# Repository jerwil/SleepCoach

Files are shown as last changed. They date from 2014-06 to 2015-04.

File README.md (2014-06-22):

# The Sleep Coach

A small simple device to help users fall asleep. The Sleep Coach was designed to be easy to manufacture, and the design and code are open source (see license at bottom).

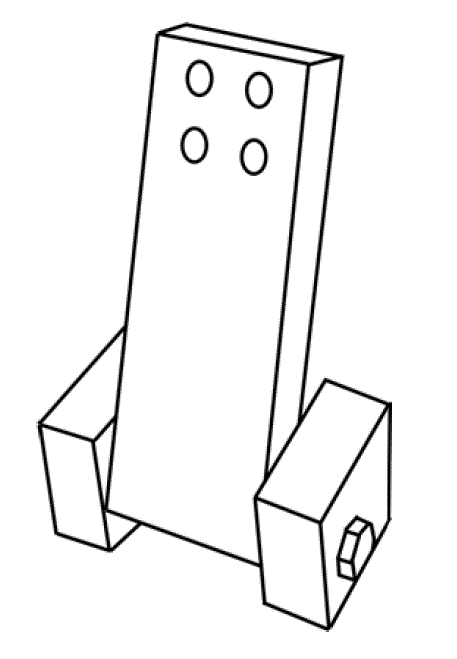
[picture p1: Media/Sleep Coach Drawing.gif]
Sleep Coach Drawing

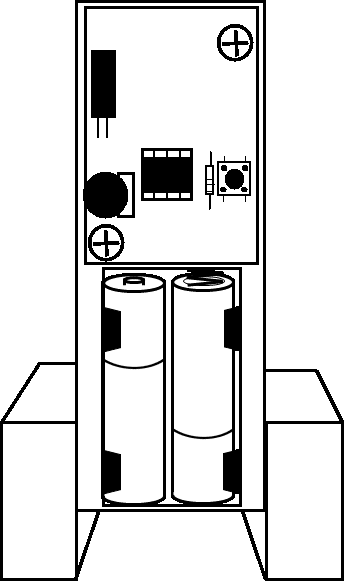
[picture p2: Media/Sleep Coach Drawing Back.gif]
Sleep Coach Back View


## Features

* Creates a pattern of light that you match your breathing to
* Breathing rate is decreased during sleep, so this helps ease you into sleep faster
* The maximum brightness can be adjusted on-the-fly using the wheel potentiometer on the back
* One-button operation

## How to Use

* Set up the sleep coach on a night stand or table next to your bed.
* Turn on the sleep coach and adjust its angle to either shine in your eyes or on a wall or ceiling.
* Begin coaching, and match your breathing to the pattern of light
* Fall asleep faster!

## Demo Video

* [Demo Video](http://youtu.be/cpdKv6ZaVtQ)

## Study

I have been conducting a study to collect data on the Sleep Coach to see if it actually helps users fall asleep.

* [Study Information](http://i.imgur.com/wzw9Kvx.jpg)
* [Study Sign-up link] (http://goo.gl/noJXXP)
* [Study Results So Far] (https://github.com/jerwil/SleepCoach/blob/master/Documentation/Data%20Summary%20-%20Round%202.pdf?raw=true)

So far I have had great success with the sleep coach, but I only have a sample size of 5 users. I'm always looking for more study participants!

## Requirements

### Hardware

* ATtiny85
* 8 pin DIP socket (recommended)
* 1-sided copper board
* 330Ω resistor
* 10 mF capacitor
* 4 red LEDs
* Tact button
* Wheel potentiometer
* Battery holder for 2 AA batteries

For my version of the mechanical design:

* 3.5" 1/4-20 bolt
* 1/4-20 wing nut
* 8 inches of 1.5" x .75" wood

Details on mechanical design to come soon

### Schematics

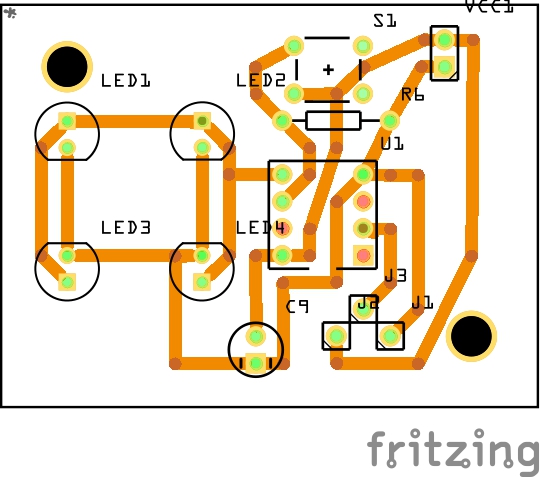
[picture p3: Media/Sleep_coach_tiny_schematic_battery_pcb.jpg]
Sleep Coach schematic


See the included Fritzing diagram (.fzz file) for details.

### License

<br /><span xmlns:dct="http://purl.org/dc/terms/" property="dct:title">MAX7219 Board Schematics</span> by <a xmlns:cc="http://creativecommons.org/ns#" href="www.JeremyAdamWilson.com" property="cc:attributionName" rel="cc:attributionURL">Jeremy Wilson</a> is licensed under a <a rel="license" href="http://creativecommons.org/licenses/by-nc/4.0/">Creative Commons Attribution-NonCommercial 4.0 International License</a>.

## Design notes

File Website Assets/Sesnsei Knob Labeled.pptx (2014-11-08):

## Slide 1

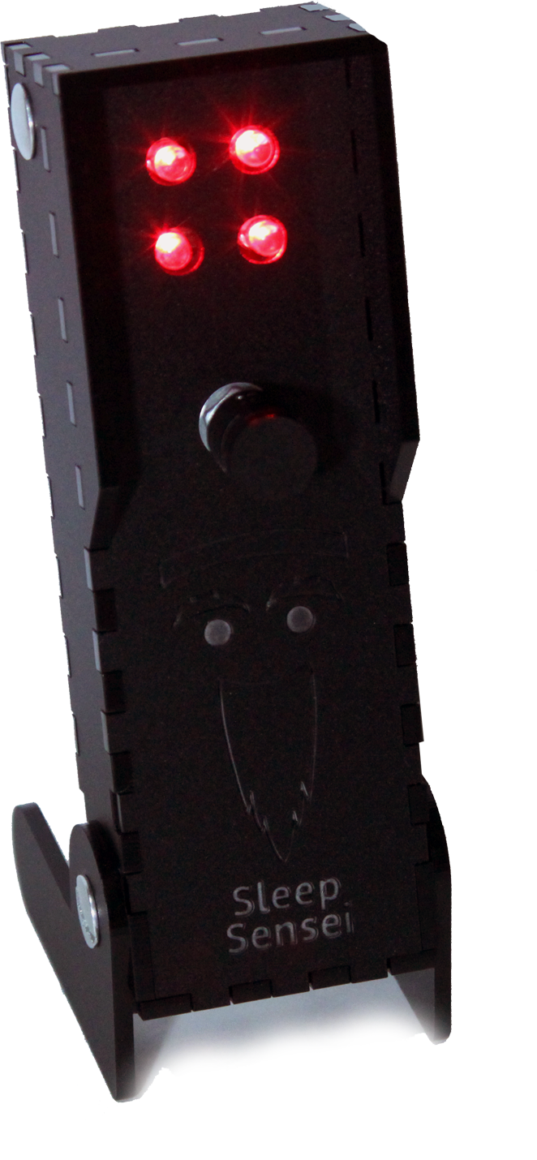
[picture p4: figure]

4 Bright LEDs
So you can be coached with your eyes closed

Side Shields
To cut down stray light

Mode Selection
Choose between profiles

Brightness Adjustment
To account for different tastes

Pivoting Base
Allows you to aim the light where it is needed

NOTE: Functional prototype – not final product

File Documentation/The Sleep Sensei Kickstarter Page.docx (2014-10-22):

# The Sleep Sensei Story

I have trouble falling asleep at night. I used to take over-the-counter remedies, and I've tried prescription stuff, but these either made me feel groggy the next day or had side effects that were not worth the benefits. I then stumbled upon some smartphone apps and devices that use a rising and falling pattern of light to help you get to sleep by training your breathing. I tried these with some success, but I found that they all had one major flaw: they required your eyes to be open. Who in the world tries to fall asleep with their eyes open?!

Using my arduino skills, I set to create a device that will help coach my breathing to ease myself to sleep with my eyes closed. Thus the Sleep Sensei was born, with its pivoting base and 4 ultra-bright red LEDs that can shine through eyelids, it aims to fix the problems of similar apps and devices.

# The Device Design

The Sleep Sensei is designed to shine a pattern of light through your eyelids. This pattern of light is used to coach your breathing pattern, which encourages your breaths to get longer as time progresses. To ensure that enough light is delivered, I put 4 LEDs on the device; however, the maximum brightness is adjustable to account for different tastes. In order to account for different heights of nightstands, I made the device able to pivot to encompass a wide range of scenarios. For those that sleep with a partner, I added side-shields to better concentrate the light to reduce any stray light that may annoy others.

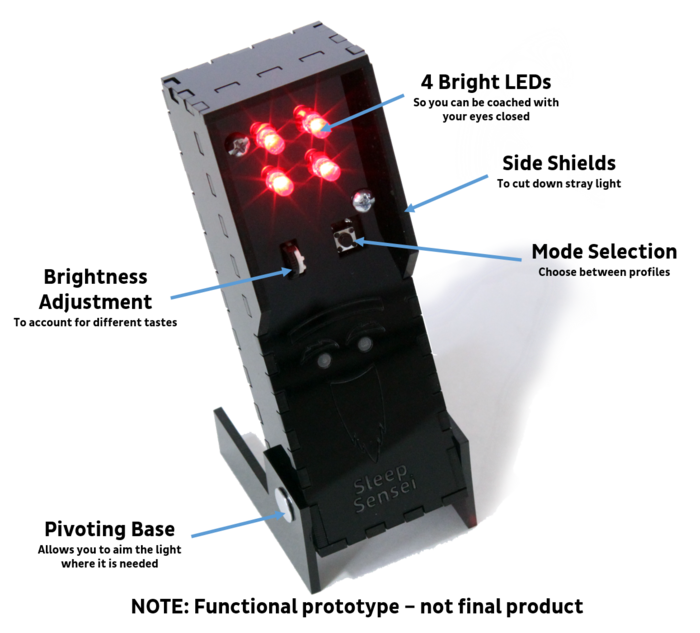
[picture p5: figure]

I chose laser cutting to make the kit easy to ship and mass produce. With the goal order volume (around 1000 units), laser cutting proved to be an affordable way to make a custom design.

The circuit board was designed with fritzing, and the logic and programming were done with arduino, which are both open source tools.

All aspects of the design (arduino code, circuit board designs, mechanical design files, website assets, photos, and documentation) are open source and are available on my github page (https://github.com/jerwil/SleepCoach). I will continue to refine the design and produce more prototypes using the Kickstarter funding, and during the development time, I encourage advanced users to fork the repository and provide me with suggestions and ideas to include in the final product!

# How it Works

The Sleep Sensei works by reducing your breathing rate, causing increased relaxation and bringing your breathing pattern closer to the reduced breathing pace that comes with sleep. It also has the benefit of giving you something to focus on for an extended period of time, which can be helpful for those with sleep troubles due to active minds.

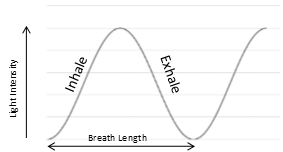
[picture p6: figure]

Using calming red light, the Sleep Sensei produces a sine wave pattern of light that you follow with your breathing. As the light begins to brighten, the user inhales, and as the light dims, the user exhales. As time passes, the breath length increases up to the maximum length specified by the user’s settings. It is a very gradual and unnoticeable change that happens progressively over time.

# Who it's for

The Sleep Sensei is for people who have trouble falling asleep. The Sleep Sensei primarily helps those with sleeping problems caused by stress or an overactive mind at bedtime. The current design of the Sleep Sensei is primarily designed for users that can lay on their side to fall asleep; however, if you must fall asleep on your back for medical or other reasons, you can still use the Sleep Sensei on an elevated surface to point down towards your eyes.

# Features

Bright and Directable Light

The main innovation of the Sleep Sensei is that it uses bright light capable of being seen through the eyelids in order to make it visible with eyes closed. Other similar products are just not bright enough to achieve this and require open eyes.

The Sleep Sensei has a pivoting base to allow you to shine the coaching light directly at the eyelids no matter how tall, short, or non-existent your nightstand is.

Adjustable Brightness

The maximum brightness of the Sleep Sensei can be adjusted any time using the adjustment wheel. This allows you to shine it on a wall for eyes-open coaching, dim it a bit if you are sensitive to light, or stare right at it for a meditation session.

Customizable Breathing Pattern

Another unique innovation of the Sleep Sensei is the user's ability to program custom breath lengths to suit their tastes and breathing rates. The user can choose initial and final breaths ranging from 4 seconds to 20 seconds long. Defaults are still available as a starting point.

Simple Design

When I set out to make this project, I was determined to make the final design as simple as possible, both to reduce cost and to make using it simple and easy.

# Feedback and the Sleep Study

When I first created the Sleep Sensei, I used it on myself for several weeks with a general feeling that it was helping me fall asleep faster. I wanted to quantify this somehow, so I began tracking my sleep using a sleep tracking app on my smartphone. After seeing a significant positive trend in the amount of time it took me to fall asleep using the Sleep Sensei, I decided that I wanted data from more users to see if the device worked for others. Thus I started the Sleep Study.

The hypothesis was simple: “The Sleep Sensei will reduce users’ average time to fall asleep.” I made posts on reddit’s /r/insomnia, /r/arduino, and /r/quantifiedself subreddits to get volunteers for the study using this advertisement (https://raw.githubusercontent.com/jerwil/SleepCoach/master/Media/Advertisement%20One%20Page.jpg) (The device used to be called the Sleep Coach). Of the 5 volunteers I was able to get, all of them showed some improvement in the time it took them to fall asleep. The full report can be found here (https://github.com/jerwil/SleepCoach/raw/master/Documentation/Data%20Summary%20-%20Round%202.pdf), and the raw data from the study can be found here (https://github.com/jerwil/SleepCoach/raw/master/Documentation/Complete%20Data%20Users%201-5.xlsx).

Some comments from the study participants:

“I think the quality of sleep has been improving, and I think that’s the Sleep Sensei. When I start having issues again I pull it out and it does help” – Alice S, TX

“I was really impressed with the Sleep Sensei- it cut the amount of time it took me to fall asleep by about half … based on the survey, I basically don’t have insomnia anymore and it feels that way” Marijke S, MA

“The Sleep Sensei allows me to fall asleep in at least under 30 minutes, sometimes even as few as 7 minutes, which is great for me! I would definitely recommend this device to anyone who is on the search for something new to help them fall asleep, someone who perhaps has tried every other sleep aid without finding anything that truly helps yet. The Sleep Sensei is awesome!” – Kate B, GA

“I’ve noticed a HUGE decrease in how long it takes me to fall asleep which has been wonderful! I really like the machine. It’s easy to use and works well.” – Kelly P, LA

Now I want to reach a much wider audience with the Sleep Sensei by launching this Kickstarter. Hopefully it will help others as much as it helped the study participants!

# Choosing the Kickstarter Goal

When I first started producing Sleep Senseis for the sleep study, I created a simple design that I could make cheaply with parts from my local hardware store. Each one was made by hand, a process that took about 90 minutes per Sleep Sensei (more if I had to troubleshoot a problem with my low-quality homemade circuit boards).

After receiving such positive feedback from the sleep study, I wanted to bring the Sleep Sensei to the masses, but I knew I couldn’t keep spending hours just to produce a dozen devices. Thus I have turned to outsourcing the circuit board manufacture and assembly as well as making the mechanical components by laser cutting. I got multiple quotes and found that I need to have at least 1000 Sleep Senseis produced in order to make them economically viable. For example, a batch of 100 circuit boards costs more than 4 times more per board than a batch of 1000 boards!

# The Timeline

Assuming the Kickstarter is fully funded, this is the plan to make Sleep Sensei a reality:

# Progress

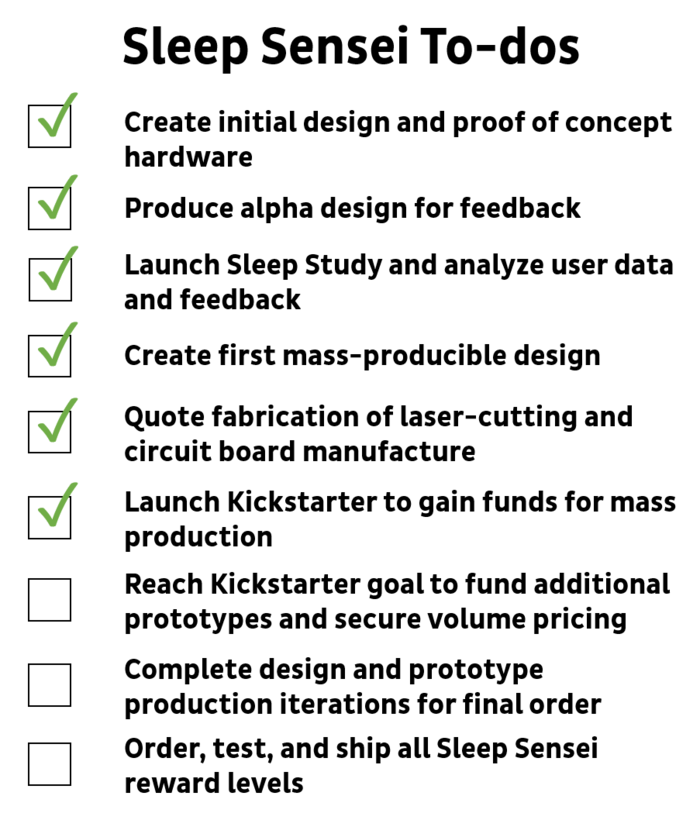
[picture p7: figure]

# Rewards Photos and Details

Note: the Sleep Sensei is still under development, so the below images will differ from the final product.

The bare board:

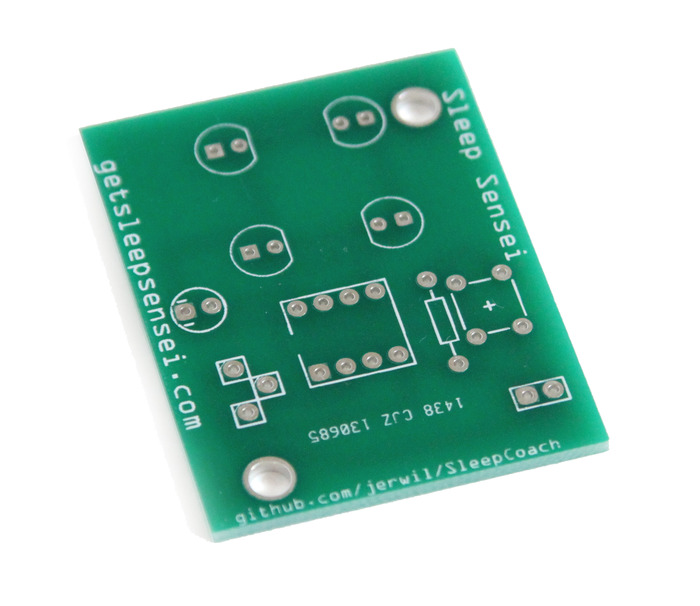
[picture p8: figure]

Just the board. Provide your own electrical components and soldering skills to complete the board, or just hang it on your keychain as a token of appreciation for helping this project become a reality.

The Sleep Sensei Kit:

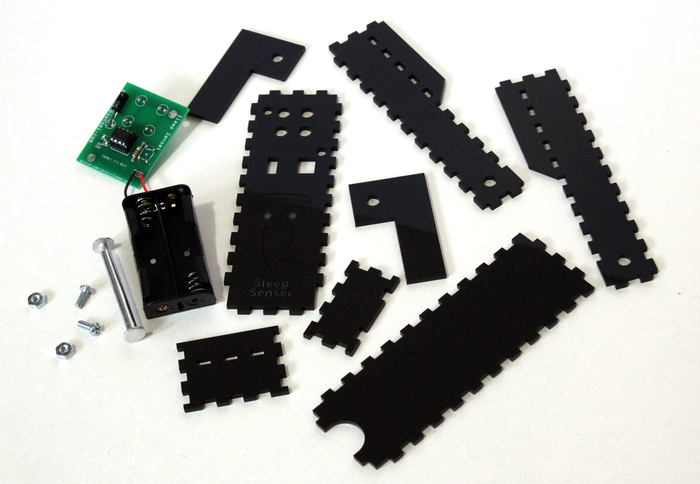
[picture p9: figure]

Includes laser-cut parts, assembled electronics board, battery pack (2 AA batteries not included), hinge hardware, and all other needed hardware (TBD). It should take less than 5 minutes to assemble.

The Assembled Sleep Sensei:

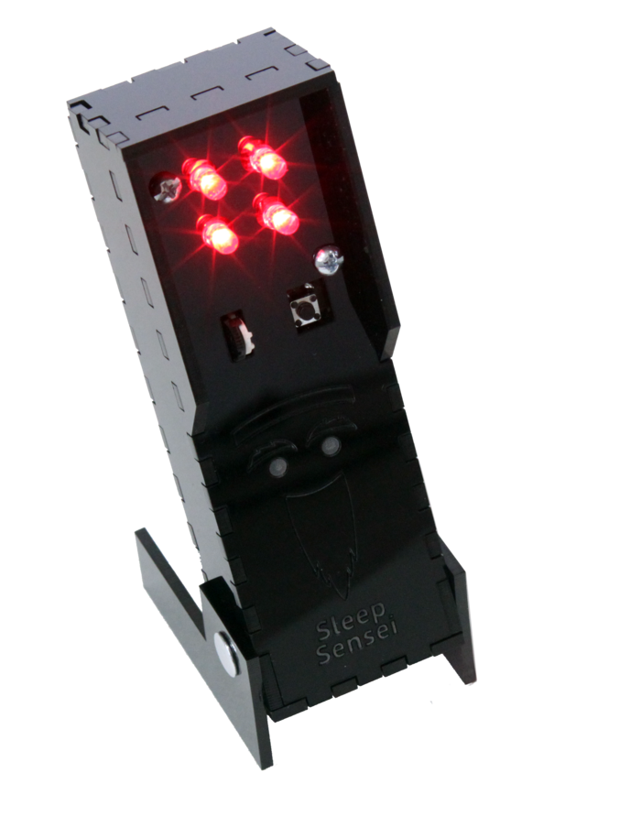
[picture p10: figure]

The fully assembled Sleep Sensei put together and fastened together by yours truly.

Logo designed by RMRDesign (https://www.fiverr.com/rmrdesign)

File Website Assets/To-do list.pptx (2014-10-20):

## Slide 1

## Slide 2

Sleep Sensei To-dos

✓

Create initial design and proof of concept hardware

Produce alpha design for feedback

✓

✓

Launch Sleep Study and analyze user data and feedback

Create first mass-producible design

✓

✓

Quote fabrication of laser-cutting and circuit board manufacture

✓

Launch Kickstarter to gain funds for mass production

Reach Kickstarter goal to fund additional prototypes and secure volume pricing

Complete design and prototype production iterations for final order

Order, test, and ship all Sleep Sensei reward levels

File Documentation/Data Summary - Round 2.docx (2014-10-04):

Sleep Coach Study – Round 2 Results

Study Premise: I created a device to try to help people fall asleep faster. I found several people willing to try the device and provide me data on their sleep via a daily survey and seep tracking smartphone app. I had the users record data for 3 weeks without the sleep coach, and I then sent the users the sleep coach device and had them record data for 3 weeks of sleep using the device.

Device Details: The Arduino-based device produces adjustable high-intensity light that can shine through your eyelids in a sinusoidally increasing and decreasing pattern of brightness with a period that lengthens over time. You match your breathing up with the intensity of the light, and over time your breathing slows.

The big problem I found with similar smartphone apps is that you need to have your eyes open to see the light, and most people do not try to get to sleep with their eyes open. I’ve designed the device to be adjustable to obtain the ideal angle of light from the nightstand to the eyes, and the max brightness is adjustable. The device is in an alpha state, meaning it isn’t pretty, but it gets the job done.

Results

User 1:

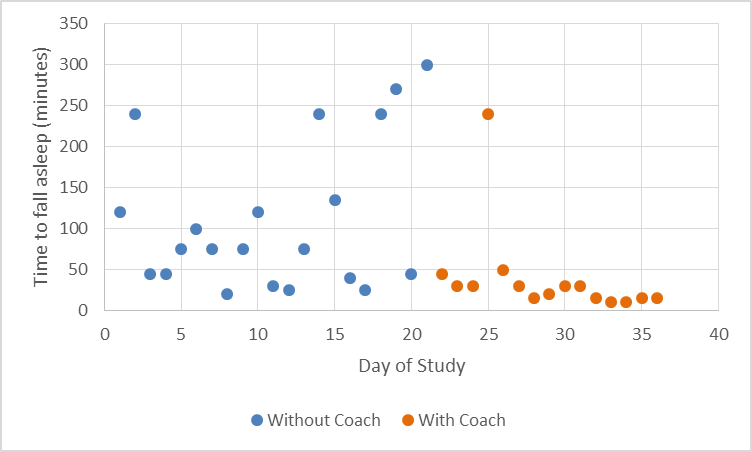
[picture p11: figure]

Average time to sleep without sleep coach: 111 minutes.

Average time to sleep with sleep coach: 39 minutes (25 minutes with outlier removed).

User Thoughts: “I think the quality of sleep has been improving, and I think that's the sleep coach.”

User 2:

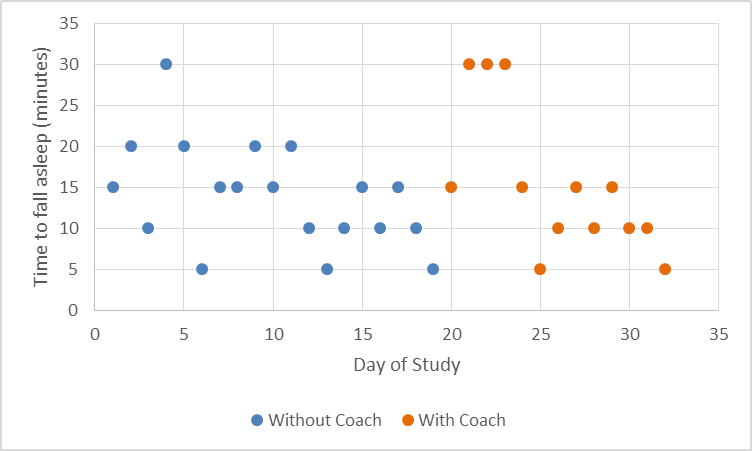
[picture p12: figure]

Average time to sleep without sleep coach: 21 minutes (14 minutes with outlier removed).

Average time to sleep with sleep coach: 15 minutes.

User Thoughts: “I was really impressed with the sleep coach- it cut the amount of time it took me to fall asleep by about half.”

User 3:

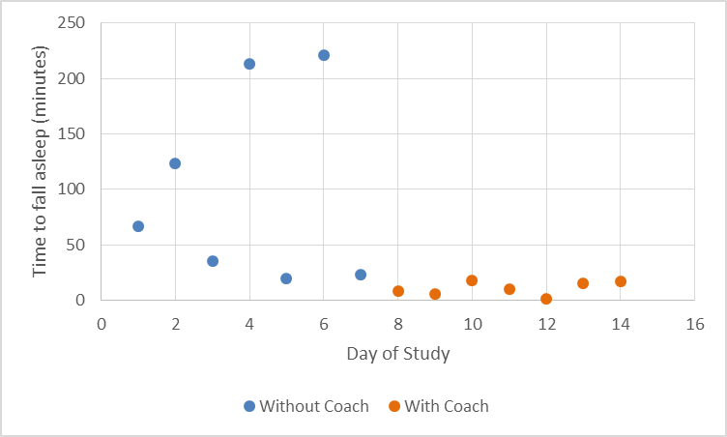
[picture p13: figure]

Average time to sleep without sleep coach: 100 minutes

Average time to sleep with sleep coach: 11 minutes.

Note: this user only provided 2 weeks of data.

New user data as of 5/25/13:

User 4:

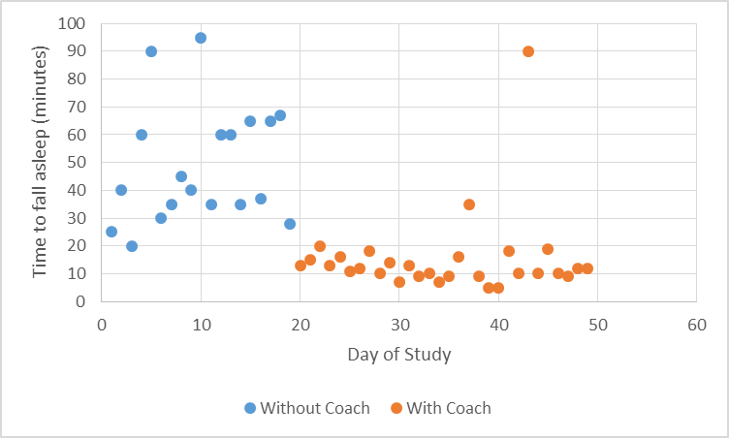
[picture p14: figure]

Average time to sleep without sleep coach: 49 minutes

Average time to sleep with sleep coach: 15 minutes (12 minutes with outlier removed).

User Thoughts: “When I am able to settle down and get in bed at a decent hour, the sleep coach helps immensely in allowing me to fall asleep in an acceptable amount of time. Usually I get incredibly distracted and it can take an hour, sometimes many hours, to fall asleep. The sleep coach allows me to fall asleep in at least under 30 minutes, sometimes even as few as 7 minutes, which is great for me! I would definitely recommend this device to anyone who is on the search for something new to help them fall asleep, someone who perhaps has tried every other sleep aid without finding anything that truly helps yet. The Sleep Coach is awesome!”

User 5:

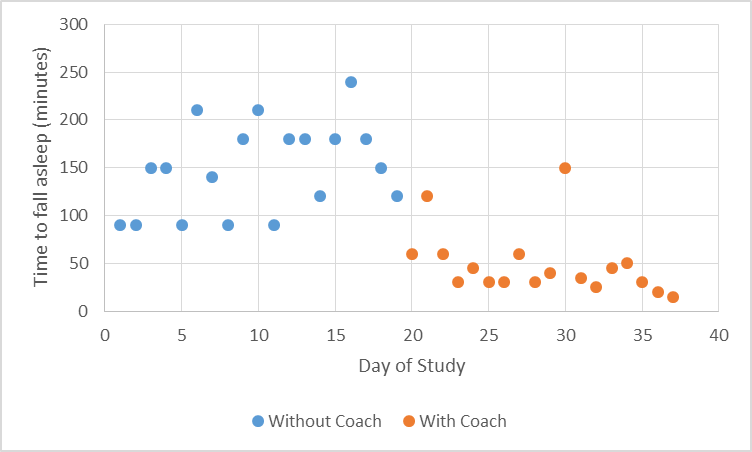
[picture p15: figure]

Average time to sleep without sleep coach: 149 minutes.

Average time to sleep with sleep coach: 49 minutes.

User Thoughts: “I've noticed a HUGE decrease in how long it takes me to fall asleep which has been wonderful! I really like the machine. It's easy to use and works well. I was worried I might not be able to see the light or that if I could it might trigger my migraines, but I can see it with no headaches caused by it. I was also expecting it to be huge for some reason, so I was pleasantly surprised by the compact size.”

User 6:

Average time to sleep without sleep coach: 19.8 minutes.

Average time to sleep with sleep coach: 8.8 minutes.

Conclusion

Similar to the last time I performed the study, actually getting data from volunteers was challenging. This time I sent out 5 sleep coaches and got reasonable data sets from 2 participants, making the total study participant count 5.

User 1 showed great improvement, and I got lots of data from this user so I can say fairly confidently that the sleep coach has improved this user’s time to fall asleep.

User 2 showed little to no improvement from the sleep coach over the 2 weeks of the study, but there is a slight trend showing that time to fall asleep may have been less for the second week indicating that the user may have been getting used to the sleep coach during the first week of use. The user feels as though their sleep has improved greatly.

User 3 showed great improvement, but the data set is quite limited. Since all data is user reported, there is no way to tell if the data is truthful or not.

User 4 showed great improvement and provided the most complete data set. This user reports that they will continue to use the sleep coach to help them fall asleep.

User 5 has had serious problems falling asleep, and the data shows that the sleep coach has helped this person consistently fall asleep faster.

User 6 shows improvement in the regularity of time to fall asleep when using the device. The device also seems to allow this user to fall asleep in under 20 minutes consistently.

Overall, the data is still promising. One thing that I have noticed is that the sleep coach seems to add consistency to participants’ time to fall asleep. Most of the users were all over the place with time to fall asleep before using the coach, and the sleep coach seems to give them a more consistent window of time in which they will fall asleep. I will continue to try to gain study participants. The switch to google forms for the surveys and sleep logs has greatly improved the organization of the study.

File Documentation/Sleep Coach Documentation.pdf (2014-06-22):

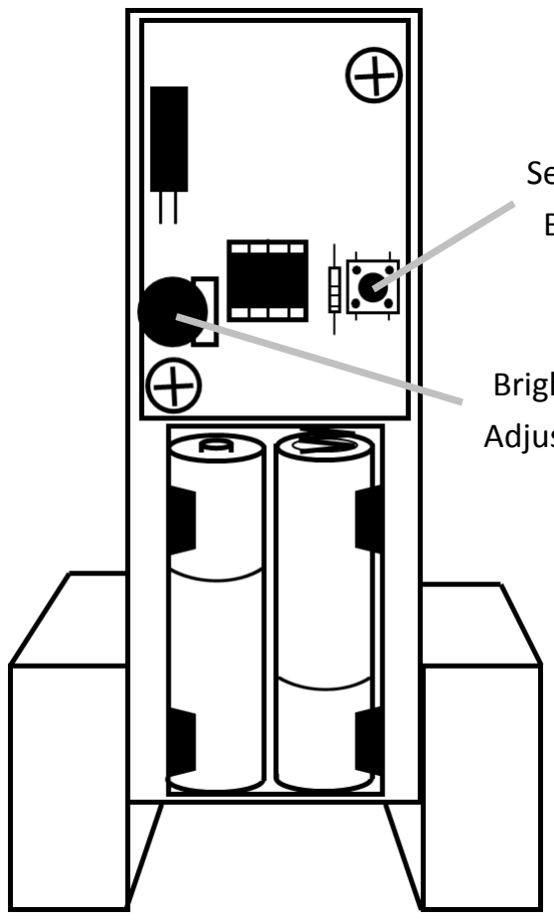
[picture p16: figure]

Brightness
Adjustment

Selection
Button

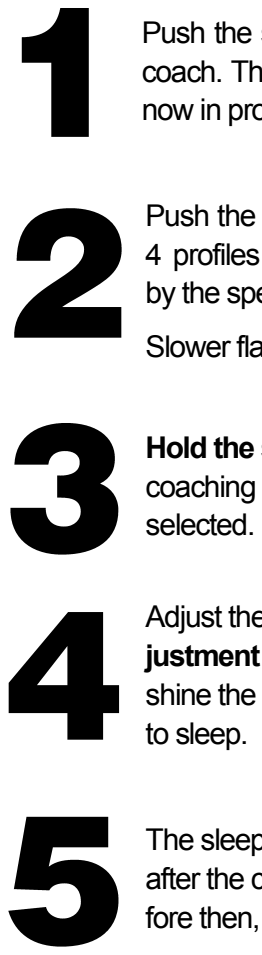
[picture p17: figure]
selected.; to sleep.

Push the selection button to turn on the sleep coach. The LED lights will begin flashing. It is now in profile selection mode.

Push the selection button to cycle through the 4 profiles and off. The profiles are indicated by the speed of the flashing lights.

Slower flashing = longer profile

Total Session
Length (min)

Initial Breath
Length (s)

Final Breath
Length (s)
7 | 6 | 10
14 | 6 | 12
21 | 6 | 14
28 | 6 | 16

Hold the selection button to begin sleep coaching once the desired profile has been

Adjust the brightness with the brightness adjustment wheel. It is recommended to shine the light through your eyelids as you try

The sleep coach will automatically turn off after the chosen profile ends. To turn it off before then, press the button.

Back View

Use calming sinusoidal patterns of light to train your breathing

How to Use the Sleep Lamp

The sleep lamp trains your breathing to help induce sleep. As the lamp increasing in brightness, breathe in. Once the brightness reaches a peak and begins to dim, breathe out. The breathing rate will get slower as time passes, with the final breath length depending on the profile chosen.

Turning on the Sleep Lamp and Choosing Profile

The default mode for the sleep lamp is a power-saving sleep mode. To turn the lamp on, simply push the button on the back of the lamp. This will bring you to the profile selection mode. The 4 different profiles are:

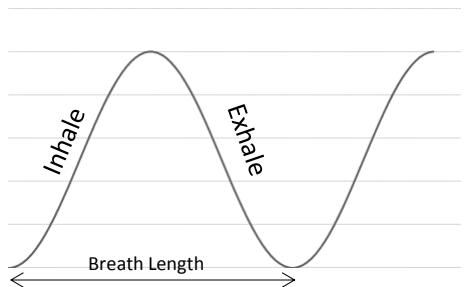
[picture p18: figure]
Breath Length

The current profile selection is indicated by how fast the lights blink. The fastest blinking pattern indicates the 7 minute session, and the slowest blinking indicates the 28 minute session. Cycle through the profiles by pushing the button. If there is no activity within 60 seconds, the lamp will enter the power-saving sleep mode. When the desired profile is reached, hold down the button for 3 seconds to begin breath coaching. To turn off the lamp during coaching, push the button. After the session, the lamp will automatically enter sleep mode.

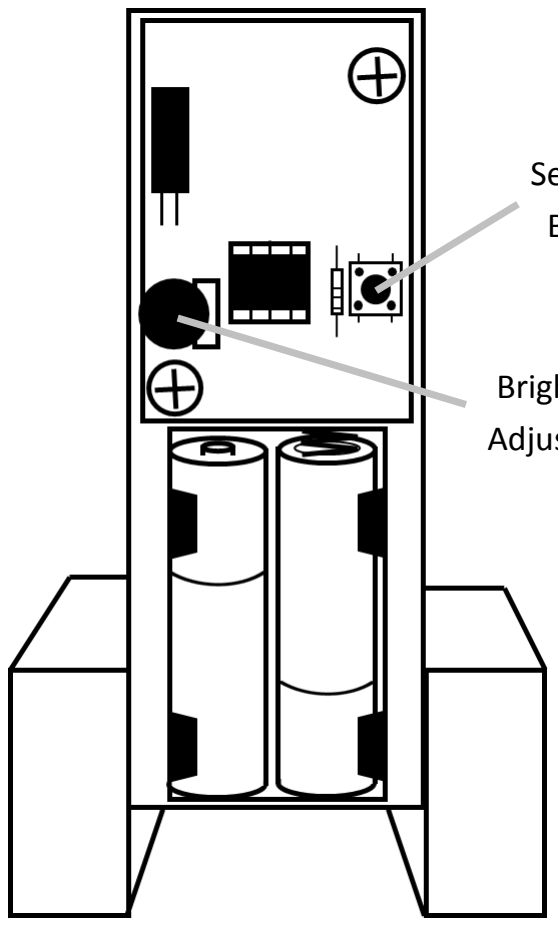
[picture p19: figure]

Brightness
Adjustment

Selection
Button

Total Session
Length (min)

Initial Breath
Length (s)

Final Breath
Length (s)
7 | 6 | 10
14 | 6 | 12
21 | 6 | 14
28 | 6 | 16

Back View

Brightness Selection

Use the brightness adjustment dial on the back of the lamp to control the maximum brightness of the lamp. There are several uses of the lamp depending on the brightness selected:

Sleep Coach With Eyes Closed - Point sleep lamp at your face and increase brightness to maximum. Close your eyes and follow the pattern of light.

Sleep Coach With Eyes Open - Point sleep lamp at ceiling or wall, lower brightness and follow pattern of light with your eyes open.

Meditation Coach - Point lamp at wall or at face. Select brightness for comfort and follow the pattern of light with eyes open or closed.

Experiment to find other uses for the lamp.

Light Intensity

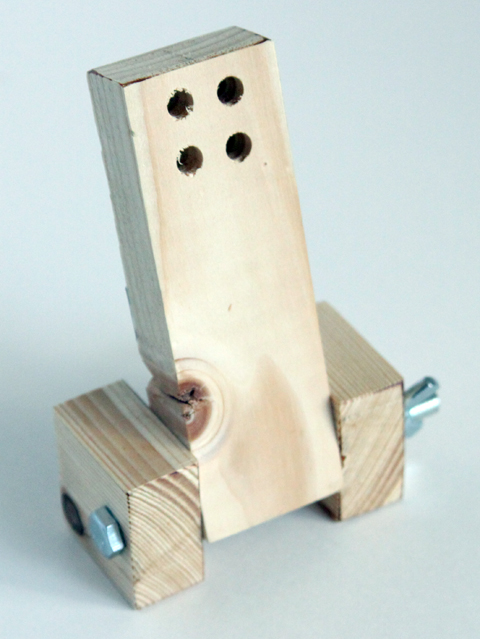
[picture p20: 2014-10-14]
Website Assets/Classic Design.jpg

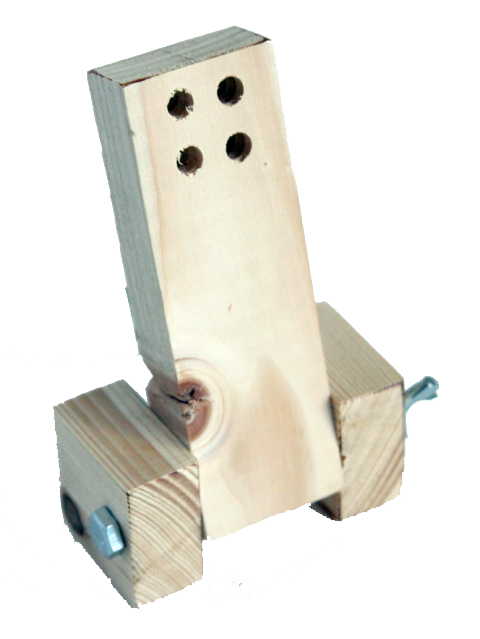
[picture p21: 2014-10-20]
Website Assets/Classic Design Transparent.png

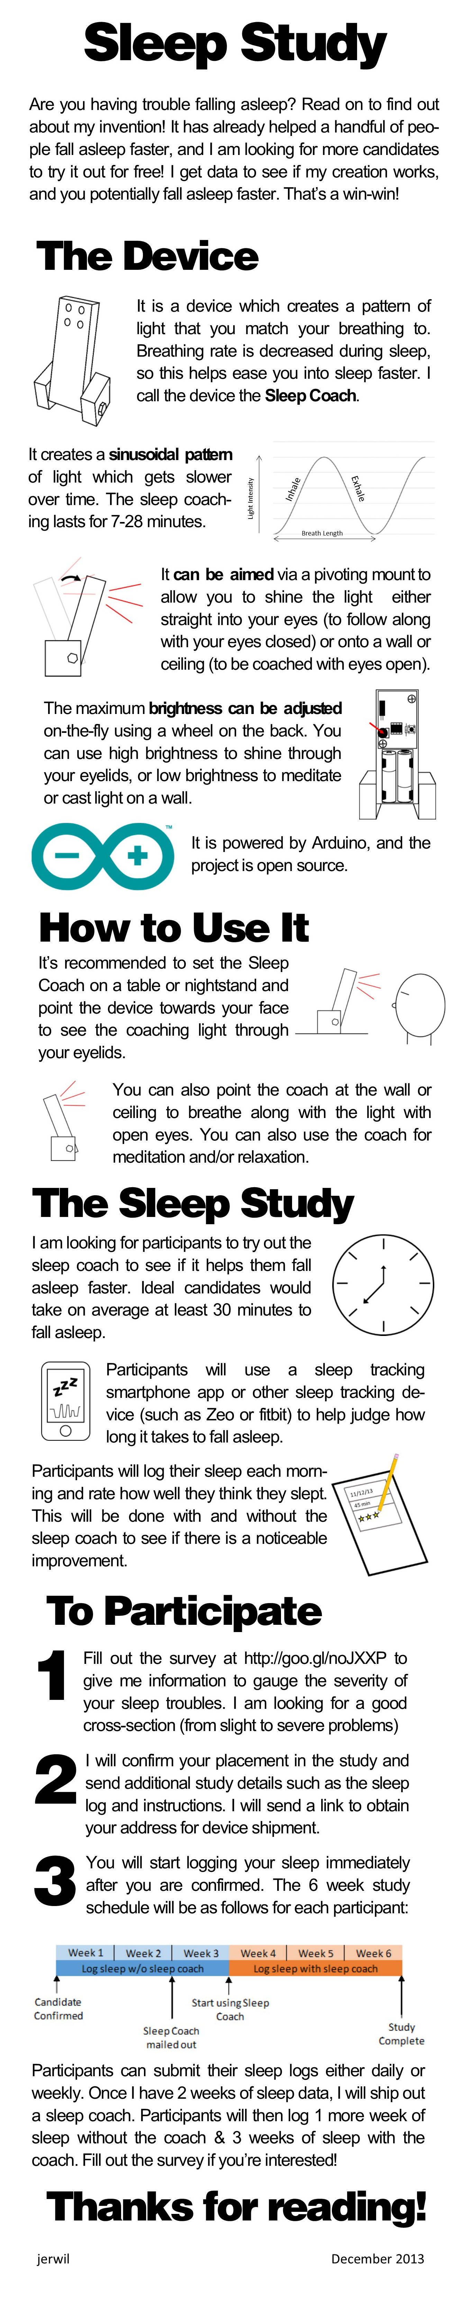
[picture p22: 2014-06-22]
Media/Advertisement One Page.jpg

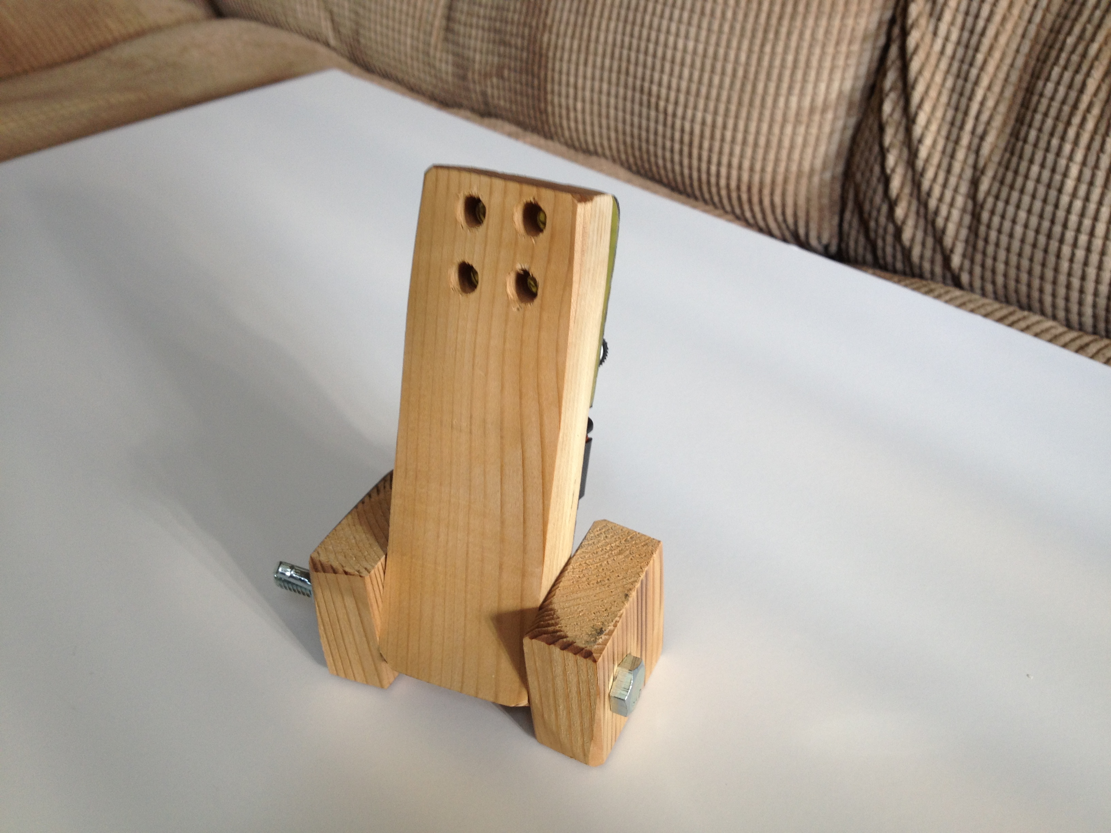
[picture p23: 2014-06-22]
Media/Isometric View.JPG

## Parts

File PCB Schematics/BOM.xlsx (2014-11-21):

#ITEM | Description | Designator | PACKAGE | Manufacturer | Manufacturer Part Number # | Supplier | Supplier Part # | QTY/BOARD | Order QTY | Price | Subtotal | Order QTY | Price
1 | Tactile Switch | S1 | THT | C&K Components | PTS645SL50-2 LFS | Mouser | 611-PTS645SL502 | 1 | 1000 | $0.09 | $87.00 | 100 | 0.127
2 | Aluminum Electrolytic Capacitors - SMD 10uF 16V | C1 | 0405 | Panasonic | EEE-1CA100SR | Mouser | 667-EEE-1CA100SR | 1 | 1000 | $0.07 | $73.00 | 100 | 0.094
3 | Thick Film Resistors - SMD 1/10watt 220ohms 1% | R1 | 0603 | Vishay | CRCW0603220RFKEA | Mouser | 71-CRCW0603-220-E3 | 1 | 1000 | $0.01 | $8.00 | 100 | 0.01
4 | Thick Film Resistors - SMD 1/20watt 10Kohms 1% 200ppm | R6,R7 | 0603 | Vishay | CRCW020110K0FNED | Mouser | 71-CRCW0201-10K | 2 | 2000 | $0.03 | $64.00 | 200 | 0.042
5 | IC & Component Sockets 8P DIP SKT 300 CL LADDER | U1 | DIP | TE Connectivity / AMP | 1-2199298-2 | Mouser | 571-1-2199298-2 | 1 | 1000 | $0.07 | $70.00 | 100 | 0.08
6 | Standard LEDs - Through Hole Red Clear 631nm | LED1, LED2, LED3, LED4 | THT | Lite-On | LTL2H3KRK | Mouser | 859-LTL2H3KRK | 4 | 4000 | $0.06 | $240.00 | 400 | 0.078
7 | Encoders 20mm Shaft Switch 24 Detents 24 Pulses | ENCODER1 | THT | Bourns | PEC12R-3220F-S0024 | Mouser | 652-PEC12R3220FS0024 | 1 | 1000 | $0.60 | $604.00 | 100 | 0.669
8 | Cylindrical Battery Contacts, Clips, Holders & Springs 2 AA W/6" WIRE LDS | VCC1 | N/A | Eagle Plastic Devices | 12BH212A-GR | Mouser | 12BH212A-GR | 1 | 1000 | $0.26 | $259.00 | 100 | 0.327
9 | Knobs & Dials BLK 15mm D-SHAFT | N/A |  | Eagle Plastic Devices | 450-AA150 | Mouser | 450-AA150 | 1 | 1000 | $0.20 | $204.00 | 100 | 0.244
10 | ATtiny85-20PU | N/A | THT | Atmel | ATtiny85-20PU | Mouser | 556-ATTINY85-20PU | 1 | 1000 | $0.79 | $791.00 | 100 | 0.96
 |  |  |  |  |  |  |  |  |  | 2.188 |  |  | 2.631

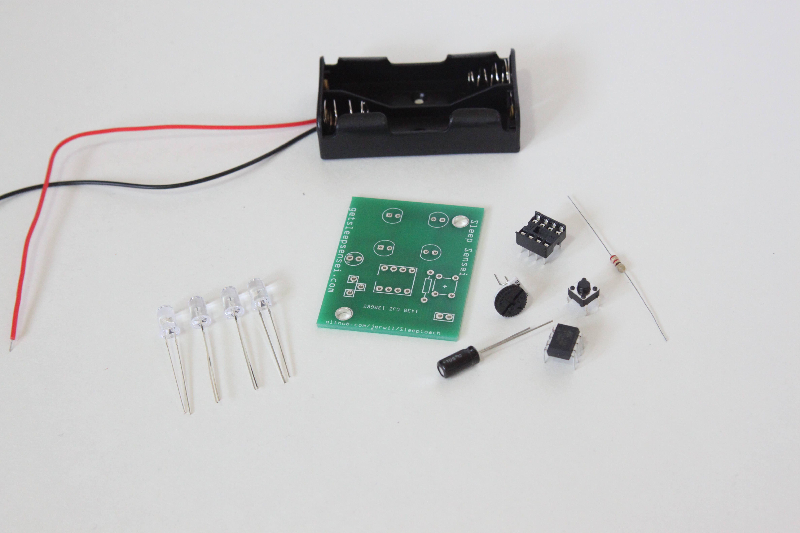
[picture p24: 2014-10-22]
Website Assets/Parts for Board.JPG

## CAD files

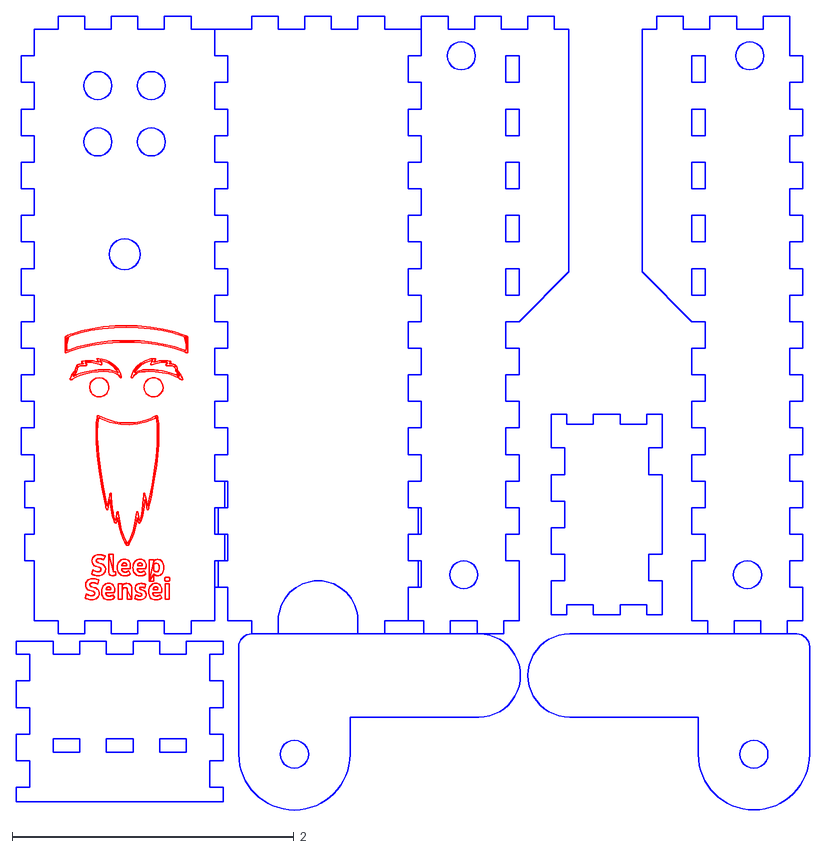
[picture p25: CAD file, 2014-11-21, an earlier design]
Mechanical Design/Archive/lasercut_rotary_encoder_11.10.14.dxf
5.63 x 5.64

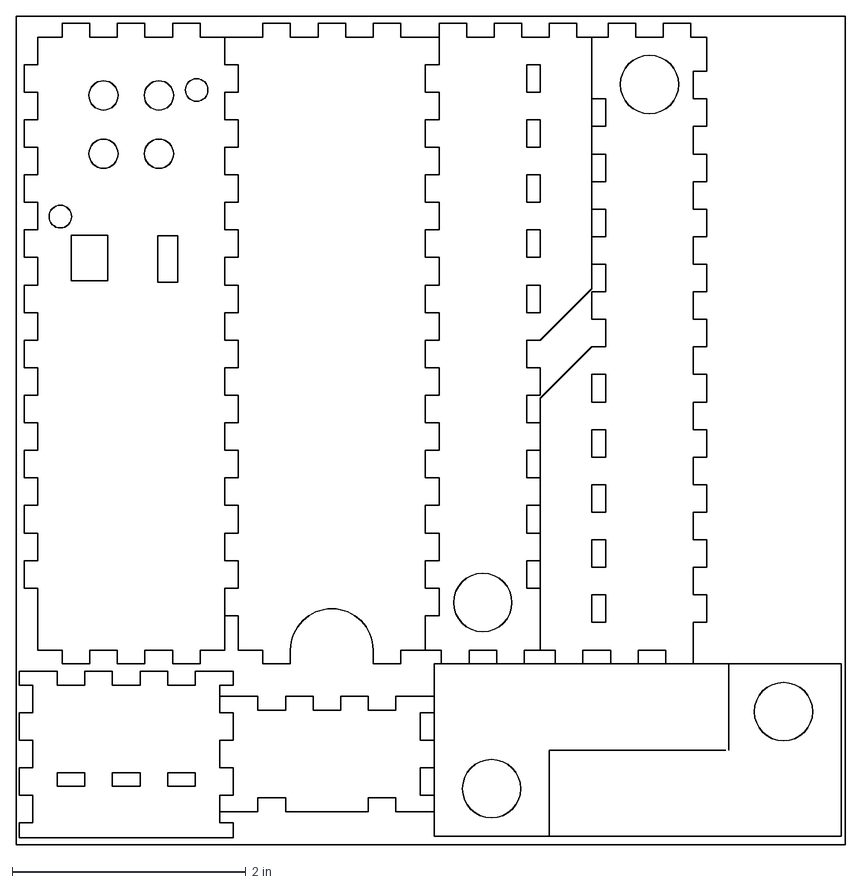
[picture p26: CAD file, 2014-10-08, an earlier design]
Mechanical Design/Archive/Lasercut Simplified for Quote Feet Econtest.dxf
7.10 x 7.10 in

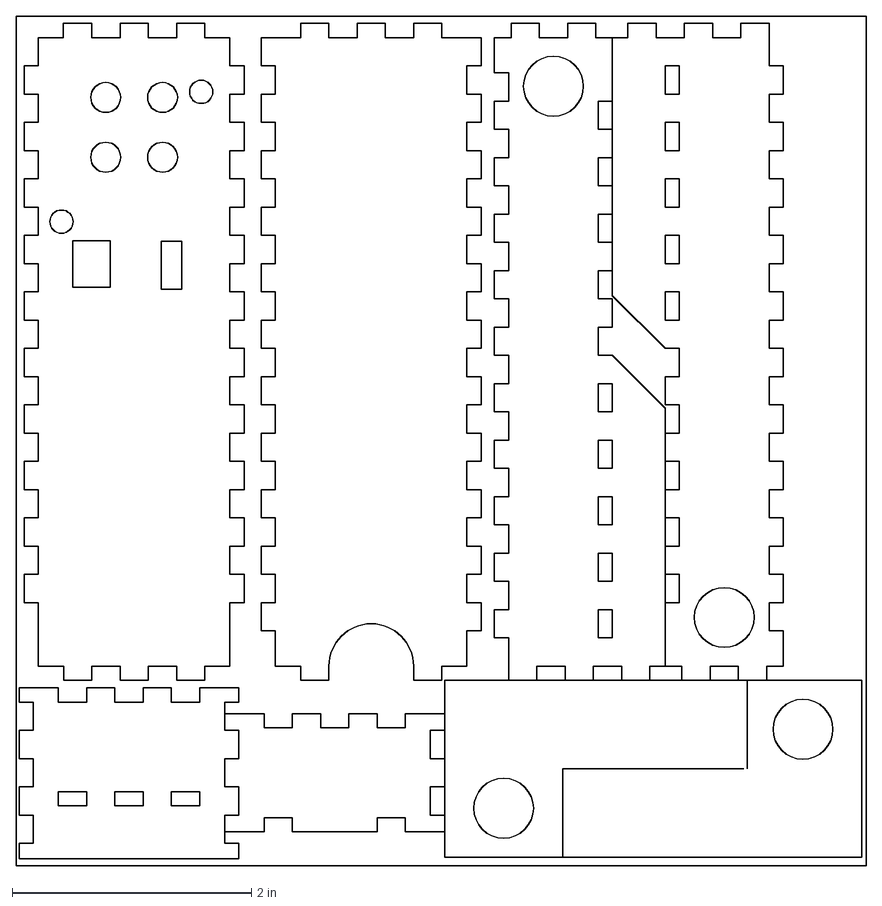
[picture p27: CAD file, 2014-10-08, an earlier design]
Mechanical Design/Archive/Lasercut Simplified for Quote Feet.dxf
7.10 x 7.10 in

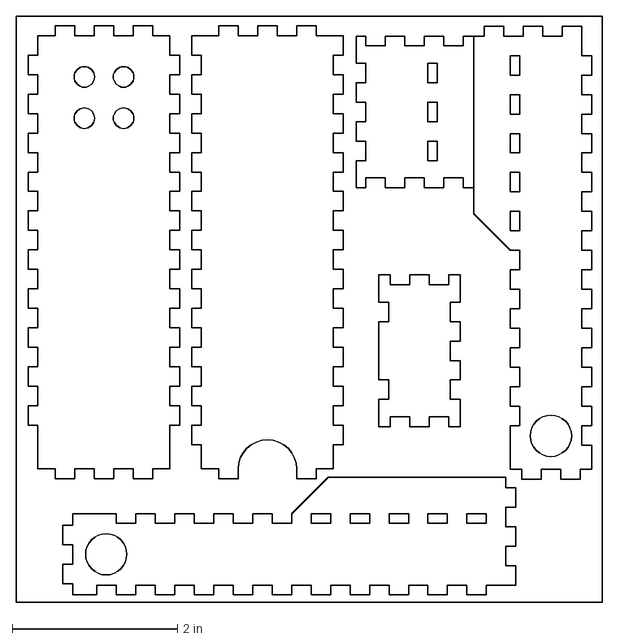
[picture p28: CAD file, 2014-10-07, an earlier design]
Mechanical Design/Archive/Lasercut Simplified for Quote.dxf
7.10 x 7.10 in

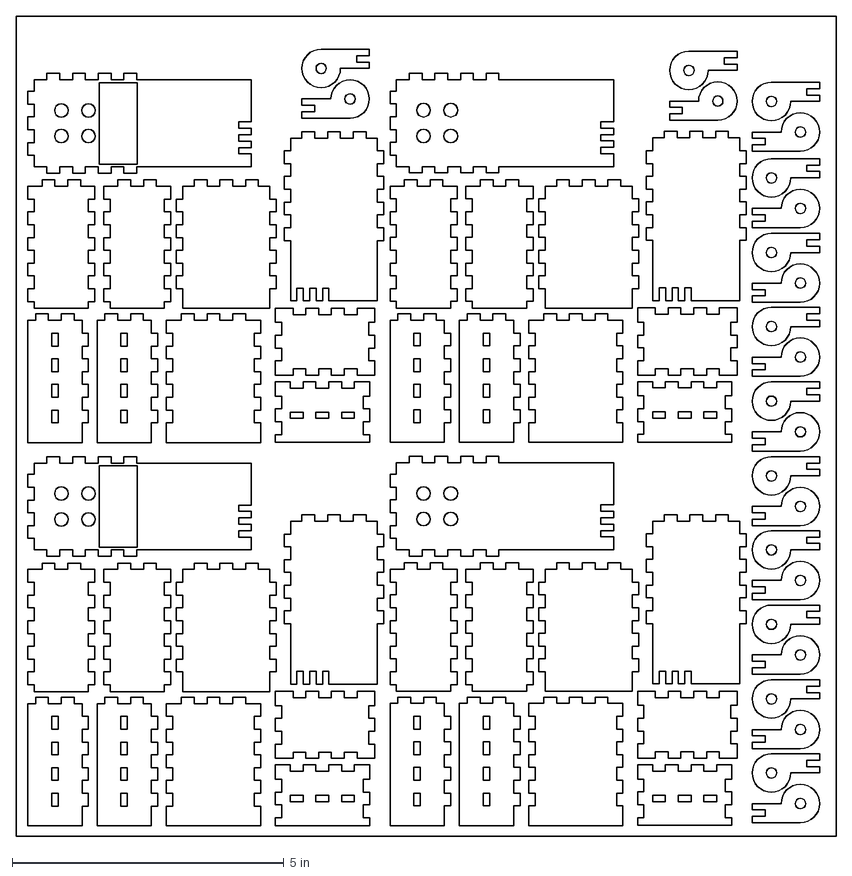
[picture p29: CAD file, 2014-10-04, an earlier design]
Mechanical Design/Archive/Lasercut.dxf
15.1 x 15.1 in

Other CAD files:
Mechanical Design/Lasercut Kickstarter Beta Version.dwg

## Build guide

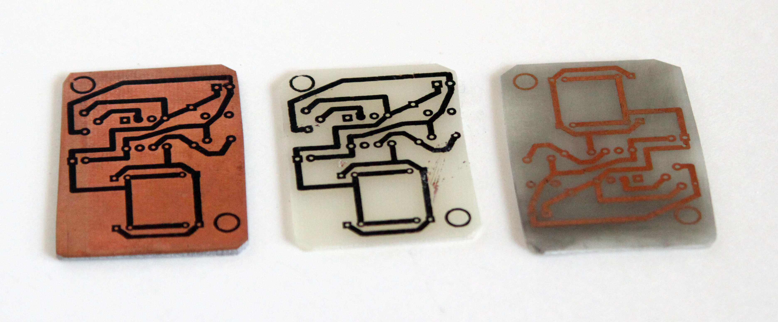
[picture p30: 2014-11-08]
Website Assets/Etch Steps.jpg

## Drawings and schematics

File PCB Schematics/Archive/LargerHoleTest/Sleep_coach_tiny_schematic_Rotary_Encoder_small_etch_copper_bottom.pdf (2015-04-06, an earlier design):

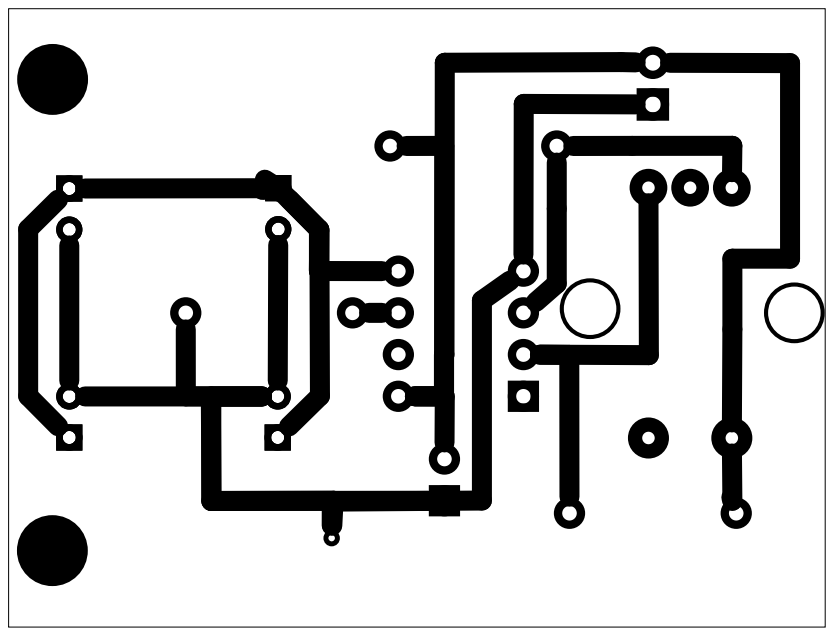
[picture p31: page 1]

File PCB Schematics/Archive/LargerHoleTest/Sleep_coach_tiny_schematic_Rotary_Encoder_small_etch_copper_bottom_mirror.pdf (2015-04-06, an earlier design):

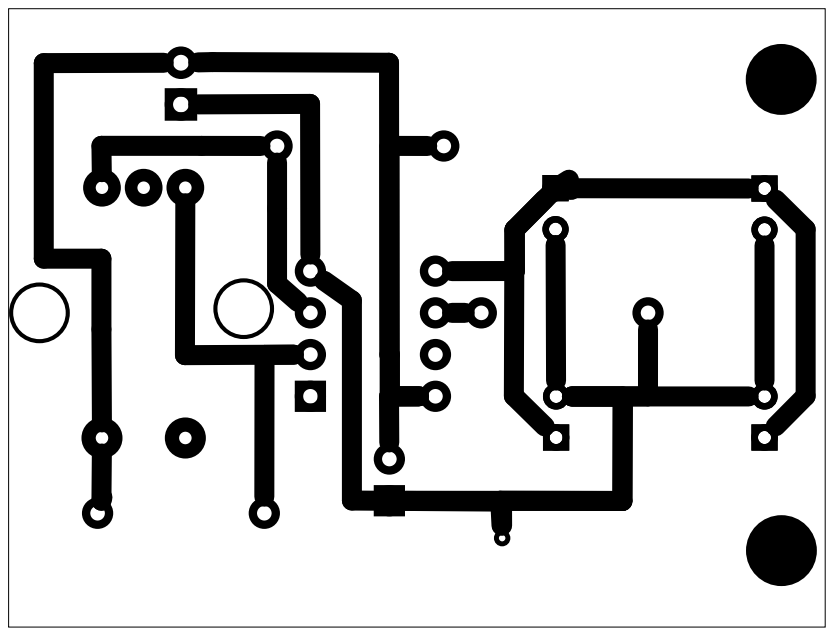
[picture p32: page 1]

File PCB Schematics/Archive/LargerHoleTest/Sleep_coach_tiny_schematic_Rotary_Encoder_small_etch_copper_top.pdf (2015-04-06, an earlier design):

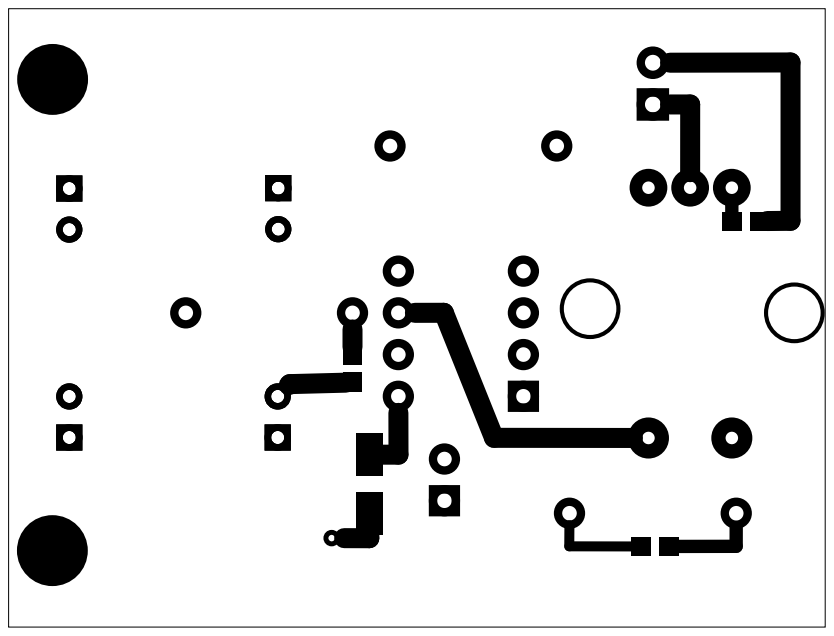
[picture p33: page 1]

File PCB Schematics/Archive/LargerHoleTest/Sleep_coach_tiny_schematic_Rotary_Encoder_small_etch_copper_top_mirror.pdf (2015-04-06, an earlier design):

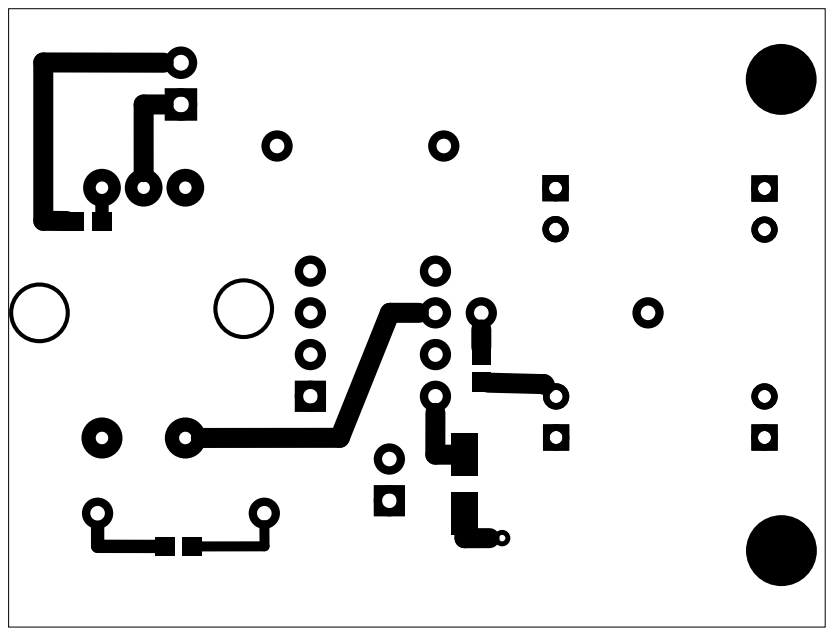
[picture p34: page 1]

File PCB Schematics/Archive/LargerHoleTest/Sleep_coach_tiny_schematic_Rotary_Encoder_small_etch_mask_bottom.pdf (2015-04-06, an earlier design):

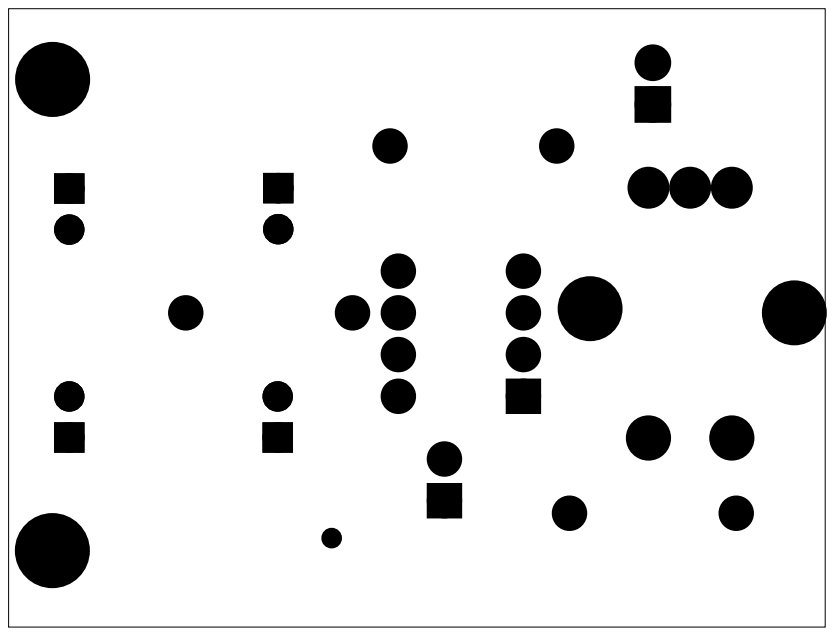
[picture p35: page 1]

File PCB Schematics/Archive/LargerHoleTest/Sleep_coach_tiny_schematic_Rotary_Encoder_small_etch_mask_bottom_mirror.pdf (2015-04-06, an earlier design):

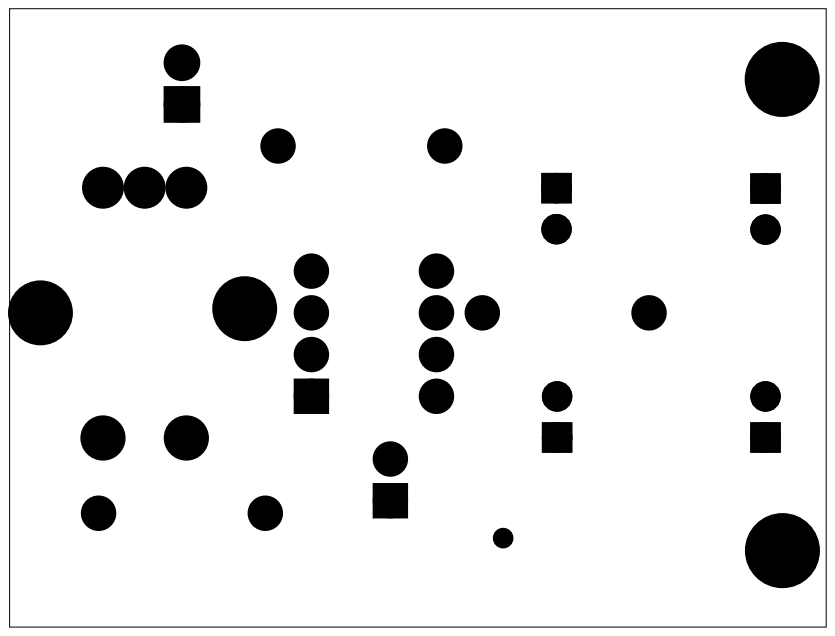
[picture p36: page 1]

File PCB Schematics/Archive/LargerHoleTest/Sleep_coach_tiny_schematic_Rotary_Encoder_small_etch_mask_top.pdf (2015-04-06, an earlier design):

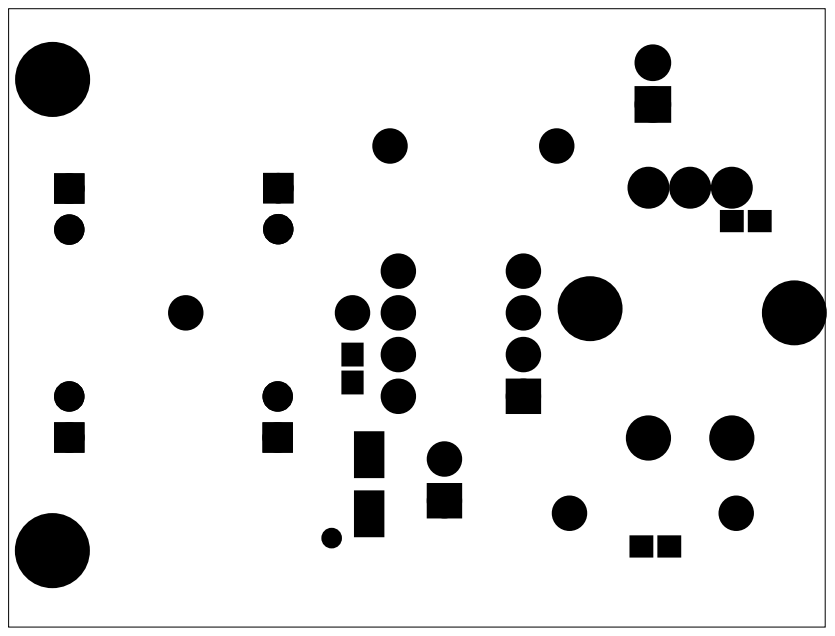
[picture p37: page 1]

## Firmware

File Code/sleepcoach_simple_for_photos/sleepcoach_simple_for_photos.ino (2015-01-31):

#include <math.h>
#include <EEPROM.h>
#include <avr/sleep.h>

// Sleep coach using ATtiny85

//Programming ATtiny85 learned from: http://www.instructables.com/id/Program-an-ATtiny-with-Arduino/step2/Wire-the-circuit/

// Setting up bits for sleep mode (from: http://www.insidegadgets.com/2011/02/05/reduce-attiny-power-consumption-by-sleeping-with-the-watchdog-timer/)

#ifndef cbi
#define cbi(sfr, bit) (_SFR_BYTE(sfr) &= ~_BV(bit))
#endif
#ifndef sbi
#define sbi(sfr, bit) (_SFR_BYTE(sfr) |= _BV(bit))
#endif



char* mode = "initialize"; // Modes are time_choose, sleep_coach, and off
// Time choose mode is where the user choses between 7, 14, 21, and 28 minutes of sleep coaching
// sleep coach mode is the mode with pulsating light
// off is when the sleep coaching is complete. A button press will bring it into time choose mode
// Intermediate modes are used to indicate switching between modes

int profile = 1;

const int LEDPin = 0;
const int pin_A = 3;  // pin 12
const int pin_B = 4;  // pin 11
const int ButtonPin = 1;

unsigned char encoder_A;
unsigned char encoder_B;
unsigned char encoder_A_prev=0;

int button_state = 0;
int button_pushed = 0; // This is the indicator that the button was pushed and released
int button_counter = 0; // This is used to detect how long the button is held for

int blink = 1; // This is used for blinking the LEDs
int blink_time = 500;
int blink_value = 254;

int timeout = 0; // This is the timeout counter
int timeout_setting = 300; // This is the setting for timeout in time_choose mode. If this is exceeded, the device will go to off mode

int brightness_mult = 9;    // how bright the LED is, start at half brightness
int fadeAmount = 1;    // how many points to fade the LED by


unsigned long currentTime;
double milis_timer[1] = {0}; // This is used to keep track of the timer used to tick for each milisecond
double second_timer[1] = {0}; // This is used to keep track of the timer used to tick for each second
double blink_timer[1] = {0};  // This is used to keep track of each half second for blinking
int ticked = 0;

int clockwise = 0;
int counterclockwise = 0;

int delay_int = 1;
int brightness = 0;
int max_brightness = 244;
double brightincrease = 1;
double k = 0.00108*5;
double k_initial = 0.00108*5;
double k_final = 0.00065;
double x = 3*3.14159/2/k; // This starts it at 0 brightness
double breath_length = 6; // The user determined breath length

// K-factors - these are used in the sine wave generation portion to change the period of the sine wave. (a k of .0054 corresponds to 6 second breath, a k of .001 corresponds to an 18 second breath) //

double k_delta = .0002; // The amount of change in k for each rotary encoder tick

double k_values[8] = {.0054, .0054, .0054, .0054, .003, .0025, .0022, .0019}; // {k1_initial, k2_initial, k3_initial, k4_initial, k1_final, k2_final, k3_final, k4_final}

int blink_times_array[4] = {250,500,750,1000}; // The delay in blinking for the four profiles during profile selection

int profile_times_array[4] = {420, 840, 1260, 1680};

int eepromwrite = 200;

int val = 200; // Current value read from EEPROM

double total_time = 420; // seconds for entire breathing coaching
double current_time = 0;

int button_press_initiate[1];     // storage for button press function
int button_press_completed[1];    // storage for button press function


void setup() {                
  pinMode(LEDPin, OUTPUT);
  pinMode(ButtonPin, INPUT);
  pinMode(pin_A, INPUT);
  pinMode(pin_B, INPUT);
  
  sbi(GIMSK,PCIE); // Turn on Pin Change interrupt
  sbi(PCMSK,PCINT1); // Which pins are affected by the interrupt
//  Serial.begin(9600); 


}


void loop() {
  
if (mode == "initialize"){
  
if (digitalRead(ButtonPin) == 1){
  eeprom_reset();
  flash_led(LEDPin, 10, 50);
}
 
else if (EEPROM.read(8) == 1){

for (int i = 0; i < 8; i++){
  val = EEPROM.read(i);
  k_values[i] = val;
  k_values[i] = k_values[i]/10000;
}
}

else {
   eeprom_reset();
}
  
mode = "time_choose";
}
  
    clockwise = 0;
    counterclockwise = 0;
    encoder_A = digitalRead(pin_A);    // Read encoder pins
    encoder_B = digitalRead(pin_B);   
    if((!encoder_A) && (encoder_A_prev)){
      // A has gone from high to low 
      if(encoder_B) {
        // B is high so clockwise
        // increase the brightness multiplier, dont go over 25
        clockwise = 1;            
      }   
      else {
        // B is low so counter-clockwise      
        // decrease the brightness, dont go below 0
         counterclockwise = 1;        
      } 
    }
encoder_A_prev = encoder_A;  
max_brightness = brightness_mult*10;

button_state = digitalRead(ButtonPin);
button_pushed = button_press (button_state, button_press_initiate, button_press_completed);
  
if (mode == "time_choose"){
  
  if (clockwise == 1){if(brightness_mult + fadeAmount <= 25) brightness_mult += fadeAmount;}
  if (counterclockwise == 1){if(brightness_mult - fadeAmount >= 1) brightness_mult -= fadeAmount;}
  
x = 0;
  
//delay(10);

if (button_pushed == 1){
profile += 1;
button_pushed = 0;
}
if (profile > 2){
profile = 0;
mode = "off";
}
  
blink_time = blink_times_array[profile-1];
 
if (tick(1000,second_timer) == 1){
timeout += 1;
if (button_state == 1){button_counter += 1;}
}

if (button_state == 0){button_counter = 0;}


if (button_state == 1){
blink = 1;
timeout = 0;
}

blink_value = max_brightness;


analogWrite(LEDPin, blink_value);



if (timeout >= timeout_setting){mode = "off";}
 
}
  
if (mode == "sleep_coach"){
  
if (clockwise == 1){if(brightness_mult + fadeAmount <= 25) brightness_mult += fadeAmount;}
if (counterclockwise == 1){if(brightness_mult - fadeAmount >= 2) brightness_mult -= fadeAmount;}
  
timeout = 0;
  
if (current_time >= total_time && brightness <= 10){
current_time = 0;
profile = 0;
mode = "off";
x = 0;
}
  
brightness = max_brightness/2*(1 + sin(k*x));
  
if (tick(delay_int,milis_timer) == 1){
  x += brightincrease;
}
if (tick(1000,second_timer) == 1){
  current_time += 1;
  k = k_initial + current_time*(k_final-k_initial)/total_time;
  if (button_state == 1){button_counter += 1;} 
}
if (x*k >= 2*3.14159){x=0;}
//else if (brightness <= 0){brightincrease = 1;}
  analogWrite(LEDPin,brightness);

if (button_state == 0){button_counter = 0;}

if (button_counter >= 3){ // If the user holds the button for 3 seconds, start the sleep coach
button_pushed = 0;
mode = "to_initial_adjust";
button_counter = 0;
}

if (button_pushed == 1 && current_time > 5){ // Turn the device off by pushing the button, but do not create false press after starting
mode = "off";
button_pushed = 0;
button_counter = 0;
current_time = 0;
profile = 0;
x = 3*3.14159/2/k; // Start it back at 0 brightness
}

}

if (mode == "to_initial_adjust"){
  
  x = 0;
  button_pushed = 0;
  flash_led(LEDPin, 5, 100);
  k = k_values[profile-1];
  mode = "initial_adjust";

}

if (mode == "initial_adjust"){

// Adjusts the initial breath length of the currently selected profile
  
if (counterclockwise == 1)
  {if(k + k_delta <= .01) 
    {k += k_delta;
    timeout = 0;}
  }
else if (clockwise == 1)
  {if(k - k_delta >= .0019) 
    {k -= k_delta;
    timeout = 0;}
  }
//k = pow(breath_length,3)*-0.000004166667+pow(breath_length,2)*0.000175000000+breath_length*-0.002583333333+0.015500000000;
brightness = 127*(1 + sin(k*x));  
if (tick(delay_int,second_timer) == 1){
  x += brightincrease;
}

if (x*k >= 2*3.14159){x=0;}

analogWrite(LEDPin,brightness);

if (tick(1000,blink_timer) == 1){
timeout += 1;
if (button_state == 1){button_counter += 1;}
}

if (button_state == 0){button_counter = 0;}

if (button_counter >= 3){ // If the user holds the button for 3 seconds, start the sleep coach
button_pushed = 0;
mode = "to_final_adjust";
button_counter = 0;
timeout = 0;
}

if (button_state == 1){
timeout = 0;
}

if (timeout >= timeout_setting){
mode = "off";
timeout = 0;
}

}

if (mode == "to_final_adjust"){
  
x = 0;
k_values[profile-1] = k;
val = k*10000;
EEPROM.write(profile-1,val);
EEPROM.write(8, 1);  
flash_led(LEDPin, 3, 100);
mode = "final_adjust";
k = k_values[profile+3];

}


if (mode == "final_adjust"){

// Adjusts the final breath length of the currently selected profile
  
if (counterclockwise == 1)
  {if(k + k_delta <= .01) 
    {k += k_delta;
    timeout = 0;}
  }
else if (clockwise == 1)
  {if(k - k_delta >= .0019) 
    {k -= k_delta;
    timeout = 0;}
  }

brightness = 127*(1 + sin(k*x));  
if (tick(delay_int,second_timer) == 1){
  x += brightincrease;
}

if (x*k >= 2*3.14159){x=0;}

analogWrite(LEDPin,brightness);


if (tick(1000,blink_timer) == 1){
timeout += 1;
if (button_state == 1){button_counter += 1;}
}

if (button_state == 0){button_counter = 0;}

if (button_counter >= 3){ // If the user holds the button for 3 seconds, start the sleep coach
button_pushed = 0;
mode = "back_to_menu";
button_counter = 0;
timeout = 0;

k_values[profile+3] = k;
val = k*10000;
EEPROM.write(profile+3,val);
EEPROM.write(8, 1);

}

if (button_state == 1){
timeout = 0;
}

if (timeout >= timeout_setting){
mode = "off";
timeout = 0;
}

}

if (mode == "back_to_menu"){
  
x = 0;  
flash_led(LEDPin, 10, 100);
button_pushed = 0;
button_counter = 0;
mode = "time_choose";

}

if (mode == "off"){
  
x = 0;

analogWrite(LEDPin,  0);  
  
system_sleep();
  
delay(1);

if (button_state == 1){ // Turn the device on by pushing the button
mode = "time_choose";
button_pushed = 0;
button_counter = 0;
timeout = 0;
}

current_time = 0;
  
}

}

int button_press (int button_indicator, int button_press_initiated[1], int button_press_complete[1]){
	if (button_indicator == 0 && button_press_initiated[0] == 1) {
	button_press_complete[0] = 1;
	button_press_initiated[0] = 0;
	}
	else if (button_indicator == 1){
	button_press_initiated[0] = 1;
	button_press_complete[0] = 0;
	}
	else {button_press_complete[0] = 0;}
return button_press_complete[0];
}

int tick(int delay, double timekeeper[1]){
currentTime = millis();
if(currentTime >= (timekeeper[0] + delay)){
	timekeeper[0] = currentTime;
	return 1;
  }
else {return 0;}
}

void tick_reset(double timekeeper[1]){
currentTime = millis();
timekeeper[0] = currentTime;
}

void flash_led(int pin, int times_to_flash, int wait_time){
  int i = 0;
  while (i <= times_to_flash){
  analogWrite(pin,244);
  delay(wait_time);               
  analogWrite(pin,0);
  delay(wait_time);
  i++;
  }
}


void eeprom_reset(){
  for (int i = 0; i < 512; i++)
  EEPROM.write(i, 0);
  for (int i = 0; i < 8; i++){
  EEPROM.write(i,k_values[i]);
  }
  EEPROM.write(8,1); 
}

void system_sleep() {
  cbi(ADCSRA,ADEN); // Switch Analog to Digital converter OFF
  set_sleep_mode(SLEEP_MODE_PWR_DOWN); // Set sleep mode
  sleep_mode(); // System sleeps here
  sbi(ADCSRA,ADEN);  // Switch Analog to Digital converter ON
}

ISR(PCINT0_vect) {
}

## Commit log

2014-06-22 Initial commit of new repo
    Moved everything to a new repo for publishing. Old repo is very
    cluttered with experimental code and boards. This repo is for tested and
    released versions of the code and PCB.
    [Sleep_coach_tiny_schematic_8_up_battery.fzz, Sleep_coach_tiny_schematic_battery.fzz]
2014-06-22 Added PCB schematic photo
2014-08-13 Added raw data and made charts consistent in doc
    Also added silk screen to PCB for production
    [Complete Data Users 1-5.xlsx, Sleep_coach_tiny_schematic_battery.fzz]
2014-09-11 Created SMD version
    Also added 6th user to data
    [Complete Data Users 1-5.xlsx, Sleep_coach_tiny_schematic_battery_SMD.fzz]
2014-10-04 Started quoting boards and lasercutting
    Created initial laser cut design for production and created some assets
    for logo creation. Also created BOM for circuit manufacture.
    [BOM.xlsx, Complete Data Users 1-5.xlsx, Lasercut.dxf, Sleep_coach_tiny_schematic_battery.fzz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]
2014-10-06 Created alternate board designs for testing
    PotSwap is for placing the potentiometer on the other side of the board,
    while CapOptions allows for use of either SMD or through hole components
    for resistor and capacitor.
    [BOM.xlsx, Sleep_coach_tiny_schematic_battery_SMD_Quote_PotSwap.fzz, Sleep_coach_tiny_schematic_battery_SMD_Quote_PotSwap_CapOptions.fzz]
2014-10-07 Added initial logos
    Logo looks a bit threatening, have asked for a revision.
    [BOM.xlsx, Lasercut Simplified for Quote.dxf]
2014-10-07 Ignore BOM changes
    [BOM.xlsx]
2014-10-07 Updated BOM
    [BOM.xlsx]
2014-10-07 Created version for new potentiometer
    Chose potentiometer that is on its side for ease of integration with
    design
    [Sleep_coach_tiny_schematic_SidePot.fzz, Sleep_coach_tiny_schematic_battery_SMD_Quote_PotSwap_CapOptions.fzz]
2014-10-08 Created new lasercut design
    Placed order for Econtest
    [Lasercut Simplified for Quote Feet Econtest.dxf, Lasercut Simplified for Quote Feet.dxf]
2014-10-08 Updated silkscreen
    [Sleep_coach_tiny_schematic_SidePot.fzz]
2014-10-18 Organized mechanical design files
    Started working on user configurable profiles for sleep coaching
    sessions. Modified board design for front controls.
    [K Calculation.xlsx, Lasercut Kickstarter Beta Version.dwg, Lasercut Simplified for Quote Feet Econtest.dxf, Lasercut Simplified for Quote Feet.dxf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]
2014-10-18 Board design accommodates SMD and TFT
    Edited board design to allow for use of through-hole components or
    surface mount. Also added a jumper for single-sided production.
    [Sleep_coach_tiny_schematic_SidePot_Options.fzz]
2014-10-19 Started concept of control with rotary encoder
    Also fixed some website assets.
    [Sleep_coach_tiny_schematic_Rotary_Encoder.fzz]
2014-10-19 Got rotary encoder code working with basic
    Need to try to adjust breath length using rotary
    [Sleep_coach_tiny_schematic_Rotary_Encoder.fzz]
2014-10-20 Organized PCB files
    Two main files - Rotary_Encoder is for use with a rotary encoder and
    will be design going forward. SidePot_Options uses a button and
    potentiometer and is designed to have both controls on front with
    laser-cut design.
    [Sleep_coach_tiny_schematic_8_up_battery.fzz, Sleep_coach_tiny_schematic_SidePot.fzz, Sleep_coach_tiny_schematic_battery.fzz, Sleep_coach_tiny_schematic_battery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]
2014-10-20 Fixed PCB per design rules check
    [Sleep_coach_tiny_schematic_Rotary_Encoder.fzz]
2014-10-22 Putting kickstarter page into repository
    Just in case
2014-11-08 Added SMD components
    Also added lots of web assets and files used for Houston Mini Maker
    Faire
    [Sine Simulation.xlsx, Sleep_coach_tiny_schematic_Rotary_Encoder.fzz]
2014-11-09 Updated BOM and silkscreen labels
    For rotary encoder version of Sleep Sensei
    [BOM.xlsx, Sleep_coach_tiny_schematic_Rotary_Encoder.fzz]
2014-11-21 Updated files for latest order
    [BOM.xlsx, SleepSensei.gbl, SleepSensei.gbo, SleepSensei.gbs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]
2015-01-03 Added reset to defaults for breath lengths
    To do this, the user removes the batteries and then re-inserts the
    batteries with the button held down. The device will blink rapidly to
    show that it was done.
2015-02-01 Basic functionality of adjusting digit working
    Adjust tens digit by incrementing/decrementing with rotary encoder, view
    current value by pressing button.
2015-02-01 Fully functional duration adjustment
    User can change tens and ones digit of duration on currently selected
    profile, and this information will be written to EEPROM. These values
    are read from EEPROM at startup if power is lost. Code is ready for
    alpha testing.
2015-02-23 Enlarged rotary encoder holes
    Also added professional photos to media
    [Sleep_coach_tiny_schematic_Rotary_Encoder_small.fzz]
2015-02-23 Reduced hole size slightly
    [Sleep_coach_tiny_schematic_Rotary_Encoder_small.fzz]
2015-04-06 Modified traces to reduce complexity
    [Sleep_coach_tiny_schematic_Rotary_Encoder_small.fzz, sleepsensei.gbl, sleepsensei.gbo, sleepsensei.gbs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]
2015-04-10 Got new logo concepts and finished traces
    [Sleep_coach_tiny_schematic_Rotary_Encoder_small.fzz, sleepsensei.gbl, sleepsensei.gbo, sleepsensei.gbs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]
